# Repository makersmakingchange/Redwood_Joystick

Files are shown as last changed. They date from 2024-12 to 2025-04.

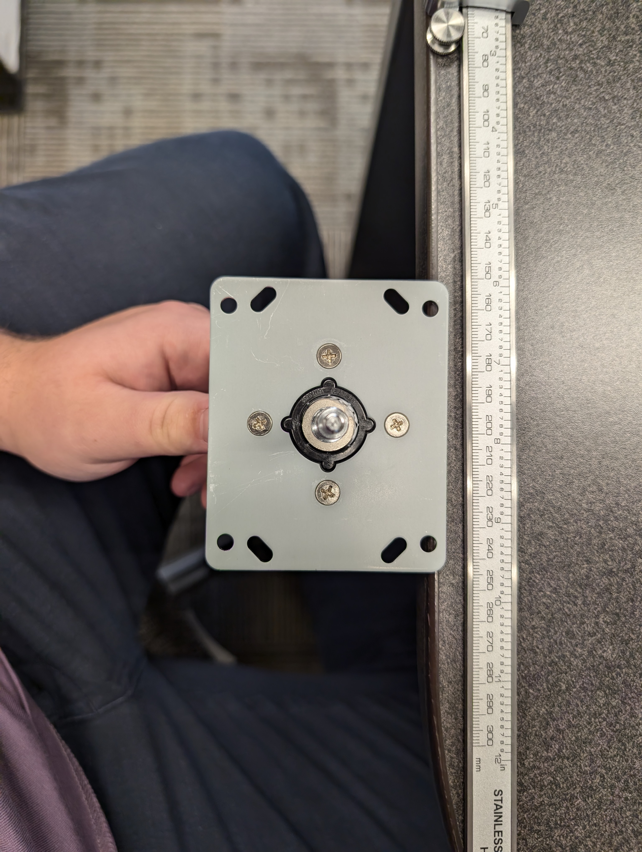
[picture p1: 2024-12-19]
Photos/Reference_Images/hold hole reference.jpg

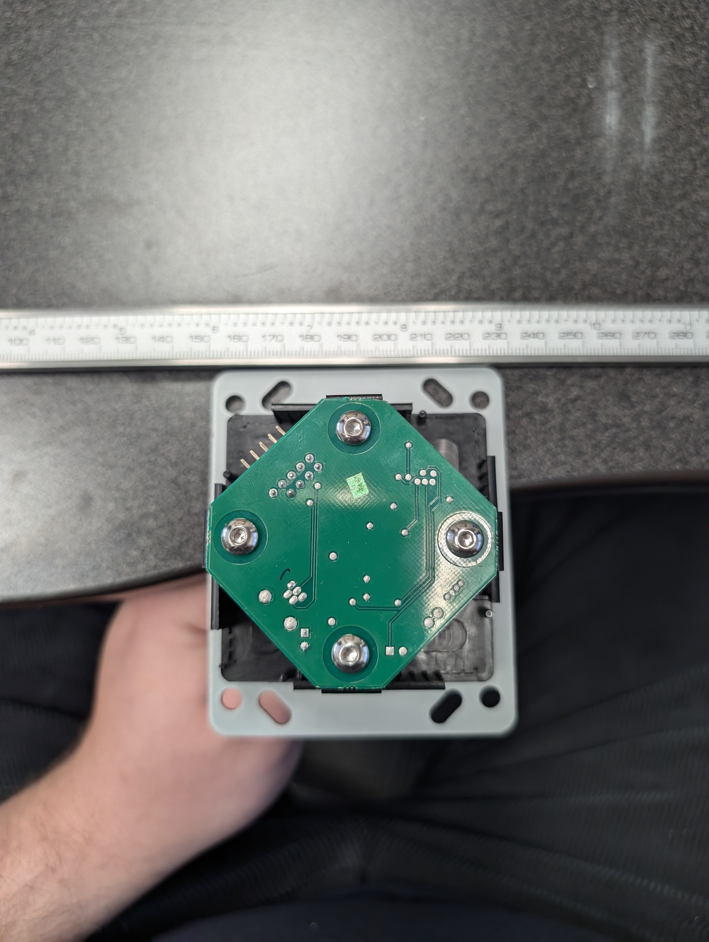
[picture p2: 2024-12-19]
Photos/Reference_Images/Reference Photo 2.jpg

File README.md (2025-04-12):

<!--- Open Source Assistive Technology: GitHub Readme Template Version 1.1 (2024-Mar-15)  --->

<!-- TITLE -->
# Redwood Joystick

<!--- SUMMARY ---> 
The Redwood Joystick is designed for users with gross motor movement and high strength, providing a durable and reliable solution for adaptive gaming and digital access. With its USB connection, it functions seamlessly as a computer mouse or gamepad, offering flexibility to suit your needs. Compatible with our [Oak Compact Joystick toppers](https://github.com/makersmakingchange/Oak-Compact-Joystick/tree/main/Build_Files/3D_Printing_Files/Toppers), it can be customized with options like goalpost or concave designs for personalized comfort. The joystick’s robust construction ensures it withstands heavy use, while its mounting adapters allow secure attachment to 1/4-20 mounting arms and 1-inch RAM mounts, ensuring a stable and accessible setup in any environment.

The device is comprised of off-the-shelf electronics, hardware, and 3D printed parts. The design uses the Ultimarc [Ultrastik analog 360 joystick](https://www.ultimarc.com/arcade-controls/joysticks/ultrastik-360-oval-top-clone/) in a robust 3D printed enclosure.

The overall cost of materials is about $97 CAD. You will need to pay customs fees if you are outside of the USA and the product can take up to 1 week to ship. Consider this in comparison to the other parts that are more readily available.

Picture of Redwood Joystick.

## More info at
- [Makers Making Change Assistive Device Library Listing](https://www.makersmakingchange.com/s/product/redwood-joystick/01tJR000006skOzYAI)

## How to Obtain the Device
### 1. Do-it-Yourself (DIY) or Do-it-Together (DIT)

This is an open-source assistive technology, so anyone is free to build it. All of the files and instructions required to build the device are contained within this repository. Refer to the Maker Guide below.

### 2. Request a build of this device

You may also submit a build request through the [Makers Making Change Assistive Device Library Listing](https://www.makersmakingchange.com/s/product/redwood-joystick/01tJR000006skOzYAI) to have a volunteer maker build the device. As the requestor, you are responsible for reimbursing the maker for the cost of materials and any shipping.

### 3. Build this device for someone else

If you have the skills and equipment to build this device, and would like to donate your time to create the device for someone who needs it, visit the [MMC Maker Wanted](https://makersmakingchange.com/maker-wanted/) section.

## Build Instructions

### 1. Read through the Maker Guide

The [Maker Guide](/Documentation/Redwood_Joystick_Maker_Guide.pdf)  contains all the necessary information to build this device, including tool lists, assembly instructions, programming instructions (if applicable) and testing.

### 2. Order the Off-The-Shelf Components

The [Bill of Materials](/Documentation/Redwood_Joystick_BOM.csv) lists all of the parts and components required to build the device.

### 3. Print the 3D Printable components

All of the files and individual print files can be in the [/Build_Files/3D_Printing_Files](/Build_Files/3D_Printing_Files/) folder.

## How to improve this Device
As open source assistive technology, you are welcomed and encouraged to improve upon the design. 

## Files
### Documentation
| Document             | Version | Link |
|----------------------|---------|------|
| Design Rationale     | 1.0     | [Redwood_Joystick_Design_Rationale](/Documentation/Redwood_Joystick_Design_Rationale.pdf)     |
| Maker Guide          | 1.0     | [Redwood_Joystick_Maker_Checklist](/Documentation/Redwood_Joystick_Maker_Guide.pdf)     |
| Bill of Materials    | 1.0     | [Redwood_Joystick_Bill_of_Materials](/Documentation/Redwood_Joystick_BOM.csv)     |
| User Guide           | 1.0     | [Redwood_Joystick_User_Guide](/Documentation/Redwood_Joystick_User_Guide.pdf)    |
| Changelog            | 1.0     | [Changelog](CHANGES.txt)     |

### Design Files
<!---
DESIGN FILES
Include a copy of the original design files to facilitate easy editing and customization. Consider also including a generic format (e.g., STEP)
--->
 - [CAD Files](/Design_Files/CAD_Design_Files)

<!---
BUILD FILES
Include a copy of the build files intended for manufacturing. This may include svg files for laser cutting, stl files for 3d printing, Gerber files for custom PCBs, and Arduino files for custom firmware
--->
### Build Files
 - [3D Printing Files](/Build_Files/3D_Printing_Files)

<!---
ATTRIBUTION
Provide any necessary attribution for designs or components that are included in the device or as part of the project.
--->
## Attribution

 - Designed by Neil Squire Society / Makers Making Change.

<!--- This is the attribution for the template. --->
 - The documentation template was created by Makers Making Change / Neil Squire Society and is used under a CC BY-SA 4.0 license. It is available at the following link: [https://github.com/makersmakingchange/OpenAT-Template](https://github.com/makersmakingchange/OpenAT-Template)

<!---
CONTRIBUTORS
List the names of the people that contributed to the design. This could include the original source of the idea, designers, testers, documenters, etc.
--->
### Contributors

Designers:
 - Tyler Fentie

<!---
LICENSE
Add the year(s) for the copyright and the Designer Name. You may use the standard set of open licenses or choose your own for the hardware, software, and accompanying materials.
--->
## License
Copyright (c) 2025 Redwood Joystick.

This repository describes Open Hardware:
 - Everything needed or used to design, make, test, or prepare the Redwood Joystick is licensed under the [CERN 2.0 Weakly Reciprocal license (CERN-OHL-W v2) or later](https://cern.ch/cern-ohl ) .
 - All software is under the [GNU General Public License v3.0 (GPL-3.0)](https://www.gnu.org/licenses/gpl.html).
 - Accompanying material such as instruction manuals, videos, and other copyrightable works that are useful but not necessary to design, make, test, or prepare the Redwood Joystick are published under a [Creative Commons Attribution-ShareAlike 4.0 license (CC BY-SA 4.0)](https://creativecommons.org/licenses/by-sa/4.0/) .

You may redistribute and modify this documentation and make products using it under the terms of the [CERN-OHL-W v2](https://cern.ch/cern-ohl).
This documentation is distributed WITHOUT ANY EXPRESS OR IMPLIED WARRANTY, INCLUDING OF MERCHANTABILITY, SATISFACTORY QUALITY AND FITNESS FOR A PARTICULAR PURPOSE.
Please see the CERN-OHL-W v2 for applicable conditions.

Source Location: https://github.com/makersmakingchange/Redwood_Joystick

----

<!-- ABOUT MMC START -->
## About Makers Making Change
[Makers Making Change Logo](https://www.makersmakingchange.com/)

Makers Making Change is a program of [Neil Squire](https://www.neilsquire.ca/), a Canadian non-profit that uses technology, knowledge, and passion to empower people with disabilities.

Makers Making Change leverages the capacity of community based Makers, Disability Professionals and Volunteers to develop and deliver affordable Open Source Assistive Technologies.

 - Website: [www.MakersMakingChange.com](https://www.makersmakingchange.com/)
 - GitHub: [makersmakingchange](https://github.com/makersmakingchange)
 - Bluesky: [@makersmakingchange.bsky.social](https://bsky.app/profile/makersmakingchange.bsky.social)
 - Instagram: [@makersmakingchange](https://www.instagram.com/makersmakingchange)
 - Facebook: [makersmakechange](https://www.facebook.com/makersmakechange)
 - LinkedIn: [Neil Squire Society](https://www.linkedin.com/company/neil-squire-society/)
 - Thingiverse: [makersmakingchange](https://www.thingiverse.com/makersmakingchange/about)
 - Printables: [MakersMakingChange](https://www.printables.com/@MakersMakingChange)

### Contact Us
For technical questions, to get involved, or to share your experience we encourage you to [visit our website](https://www.makersmakingchange.com/) or [contact us](https://www.makersmakingchange.com/s/contact).
<!-- ABOUT MMC END -->

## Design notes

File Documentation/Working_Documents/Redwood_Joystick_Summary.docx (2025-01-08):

# Overview

The Device Summary is intended to be a detailed summary of the device, product and maker information for the Redwood Joystick, making it easier to add to the Makers Making Change website. It is intended for anyone who will view the device listing.

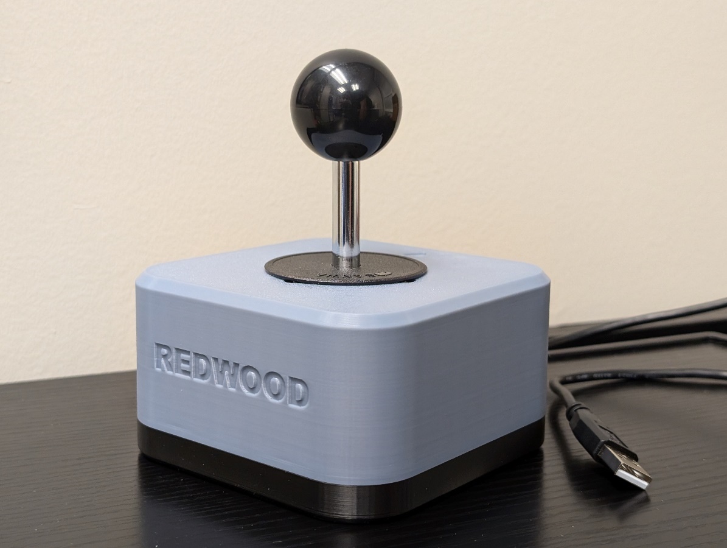
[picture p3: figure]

# Product Information

## Product Name

Redwood Joystick

## Device Category

| Adapted Toys
| Aids for Daily Living (ADL)
| Assistive Switches
| Communication Aids (AAC)
| Computer Access
| Environmental Controls
x | Gaming
| Keyguard
| Kits
| LipSyncs
| Mounting
| Recreation and Leisure
| Seating and Positioning
| Switch Interfaces
| Writing Aids
x | joysticks

## User Value Statement

The Redwood Joystick is a robust analog USB joystick designed for users with gross motor movement and high strength. Its durable build ensures reliable performance for digital access and adaptive gaming.

## Designer

Tyler Fentie – Makers Making Change

# Device Information

## Overview

The Redwood Joystick is designed for users with gross motor movement and high strength, providing a durable and reliable solution for adaptive gaming and digital access. With its USB connection, it functions seamlessly as a computer mouse or gamepad, offering flexibility to suit your needs. Compatible with our Oak Compact Joystick toppers, it can be customized with options like goalpost or concave designs for personalized comfort. The joystick’s robust construction ensures it withstands heavy use, while its mounting adapters allow secure attachment to 1/4-20 mounting arms and 1-inch RAM mounts, ensuring a stable and accessible setup in any environment.

## Disability Type

x | Agility / Dexterity
x | Arthritis
x | Cognitive
| Hearing
x | Mobility
x | Pain
x | SCI
| Vision
| Other

## Disability Type Description

The Redwood Joystick is ideal for individuals with strong gross motor movement but limited fine motor control or targeting accuracy. This includes users with conditions such as cerebral palsy, some forms of muscular dystrophy, or individuals with spinal cord injuries or post-stroke conditions who retain significant strength in larger muscle groups. Designed for those who can manage more forceful or broad movements, the joystick offers a durable, stable solution for both adaptive gaming and digital access.

## How To Use

The Redwood Joystick is simple to use. Connect the joystick’s USB Type A input to a compatible device, such as a phone, computer, Xbox Adaptive Controller, or Hori Flex Controller. See user guide for full compatibility. Once plugged in, the joystick allows you to control the device mouse or joystick input. It can be used for navigating digital interfaces, gaming, or other applications requiring joystick input, providing a reliable and easy-to-use solution.

## Estimated Cost

The estimated material cost of the device for a single build:

| $0 - $10
| $11 - $25
| $26 - $50
x | $51 - $100
| $101 - $250
| $250+

## Attribution

Designed by Neil Squire Society / Makers Making Change

Contributors

- Tyler Fentie, Neil Squire. Design and documentation.

The documentation template was created by Makers Making Change / Neil Squire and is used under a CC BY-SA 4.0 license. It is available at the following link: https://github.com/makersmakingchange/OpenAT-Template

Design inspired by SCCR Rehabilitation Engineering: https://www.printables.com/model/268854-ultrastik-analog-joystick-enclosure

# Maker Information

## Project Skills

x | 3D Printing
| Custom PCB
| Electronics
| Laser Cutting
| Mechanics
| Software
| Soldering
| Woodworking
| Other

## Skills Description

3D print the provided enclosure files and assemble the components using common hand tools (Screwdriver and plyers). With basic assembly skills and access to a 3D printer, you can quickly create a fully functional Redwood Joystick.

## Tools Needed

| 3D Printer
x | Common Hand Tools
| Common Power Tools
| Laser Cutter
| Soldering Iron
| Specialized Tooling

## Print time (hrs)

3hrs 2min

## Assembly time (hrs)

0.5hrs

## Build Instructions

To build the Redwood Joystick, start by 3D printing the enclosure using the provided design files. Once the enclosure is ready, gather the joystick components and common hand tools such as a screwdriver and pliers. Assemble the joystick by attaching the Ultimarc UltraStik 360 to the enclosure, securing the wiring, and mounting any desired Oak Compact Joystick toppers using the Topper Adapter Nut. If needed, attach the mounting adapters for RAM or 1/4-20 camera mounts. Finally, connect the joystick via USB to test functionality and ensure smooth operation. The process is straightforward, requiring only basic tools and assembly skills.

- Top and bottom 3D printed enclosure
- Ultimarc Ultrastik 360
- Optional: Oak toppers
- Optional: Mounting adapters for RAM or ¼-20 Camera mount

## Download Link

https://github.com/makersmakingchange/Redwood_Joystick/archive/refs/heads/main.zip

## Project Link

https://github.com/makersmakingchange/Redwood_Joystick

# License

## License

Hardware: CERN OHL-W

Documentation: CC BY SA 4.0

© 2024 by Neil Squire. This work is licensed under the CC BY SA 4.0 License: http://creativecommons.org/licenses/by-sa/4.0 Files available at https://github.com/makersmakingchange/Redwood_Joystick/tree/main Page 1 of 2

V1.0 | Dec 2024 Redwood Joystick Summary

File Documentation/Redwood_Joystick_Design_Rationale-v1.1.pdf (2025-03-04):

V1.0 | August 2024

## Redwood Joystick

## DESIGN RATIONALE

© 2024 by <Author>.
This work is licensed under the CC BY SA 4.0 License: http://creativecommons.org/licenses/by-sa/4.0
Files available at <Replace with MMC Library Link> | Page 1 of 43

### Introduction

- There are several joystick options in the MMC library, but there currently is not a bigger or more durable than the Oak Joystick
- The Ultrastik Joystick is bigger option but does not come with an enclosure.
- Several enclosure options exist, but are either commercial or not optimized for makers.

User focus:
- Gamers with gross motor movement and high strength

## DESIGN RATIONALE

Files available at <Replace with MMC Library Link> | Page 2 of 43

### Research

### Commercial options

Title | Quadstick Ultrastik 360
Link | Quadstick (https://www.quadstick.com/shop/ultimarc-utrastik-360-enclosure)
Author | Quadstick - Fred
License | Commercial
Cost | $204 CAD
Notes | Most popular solution for getting Ultrastik’s in North America
Title | Ultra-Stik
Link | https://oneswitch.org.uk/page/shop-ultra-stik
Author | Barrie Ellis – OneSwitch
License | Unknown
Cost | $174 CAD
Notes | Most popular solution for getting Ultrastik’s in Europe

### DIY designs

Title | OneSwitch – DIY [Instructions ONLY]
Link | OneSwitch - DIY (https://oneswitch.org.uk/art.php?id=73)
Author | Barrie Ellis – OneSwitch
License | N/A
Cost | Free
Test Build (Y/N) | N/A
Add to Library (Y/N) | No but credit them in this design
Notes
Title | UltraStik – SCCR
Link | SCCR Printables (https://www.printables.com/model/268854-ultrastik-analog-joystick-enclosure)
Author | SCCR – Rachelle Bernier
License | CC attribution-shareAlike
Cost | $100 CAD
Test Build (Y/N) | N/A
Add to Library (Y/N) | No but credit them in this design
Notes
Title | Ultrastik - Gearhead
Link | Gearhead Printables (https://www.printables.com/model/510023-housing-for-ultimarc-ultrastik-360)

## DESIGN RATIONALE

Files available at <Replace with MMC Library Link> | Page 3 of 43
Author | Gearhead (printables username)
License | GNU v2.0
Cost | $100 CAD
Test Build (Y/N) | N/A
Add to Library (Y/N) | N
Notes

## DESIGN RATIONALE

Files available at <Replace with MMC Library Link> | Page 4 of 43

### Requirements

### Goals

G01 | Act as a larger and durable form factor for our joystick line.
G02 | Provide an option for users who are breaking the internals of the Oak Joystick.
G03 | Maker manufacturable in quantities of one.
G04 | The use of support material in 3d printed components should be minimized.
G05 | The number of different filament types should be minimized.
G07 | Material costs should be minimized as to provide a low cost options (Less than or equal to $100 CAD)

### Functional Requirements

F01 | The joystick shall be usable from a the distance given by the USB cable supplied by UltraStik
F02 | The joysticks shall be compatible with the Xbox Adaptive Controller.
F03 | Joysticks shall be PC compatible.
F04 | The joystick shall denote use orientation.
F05 | The joystick shall have a range of easily interchangeable toppers.
F06 | Toppers shall not interfere with the regular physical motion of the joystick.
F07 | Toppers shall have a secure connection to the joystick.
F08 | The joystick shall be designed to be used by either hand.
F09 | Joystick shall remain stable when in use.
F10 | The housing shall protect internal components from outside sources.
F11 | Joystick designs shall support camera mounting styles.
F12 | Joystick designs shall support hook and loop fastener mounting styles.
F13 | Joystick designs shall support tabletop mounting styles with no fasteners.
F14 | Enclosure shall work with the Ultrastik joystick component

### Non-functional Requirement

NF01 | Documentation should be maintainable with the use of commonly available software.
NF02 | Documentation must be available in a digital format.
NF03 | Documentation must be printable.
NF04 | Documentation, code, and hardware must have appropriate open-source licenses.
NF05 | Instructions must be provided for using joystick with XAC for gaming
NF06 | Instructions must be provided for using joystick with PC/Phone/Tablet for gaming
NF07 | Instructions must be provided for using joystick with PC/Phone/Tablet for digital access

### Constraints

C01 | Joystick must be maker manufacturable.
C02 | Not for use with mobility devices.
C03 | The joystick shall be based on the commercially available Ultrastik 360 Analog Joystick.
C04 | The Ultrastik 360 Analog Joystick has an approximate activation force of 298 grams.

## DESIGN RATIONALE

Files available at <Replace with MMC Library Link> | Page 5 of 43
C05 | The Ultrastik 360 Analog Joystick has an X and Y axis range of ±15.5°
C06 | The Ultrastik 360 Analog Joystick has a linearity of TBR (no info from manufacturer)
C07 | The Ultrastik 360 Analog Joystick has a mechanical lifecycle of TBR (no info from manufacturer)
C08 | The Ultrastik 360 Analog Joystick has an operating temperature range of TBR (no info from manufacturer)
C09 | 3D printed components shall be printable within a 180x180x180mm print volume.

## DESIGN RATIONALE

Files available at <Replace with MMC Library Link> | Page 6 of 43

### Ideation

- Prevent using screws coming from the top enclosure if possible
- This may be able to be prevented with the use of the dust cover. Need to investigate
- The top of the joystick component should allow room for the dust cover
- No easily source able size of bolt will allow for a design where the bolt comes through the bottom side of the joystick component into a enclosure without spacers
- Toppers
- Use Oak toppers by adapting the 3D printed nut to fit onto the ultrastik

## DESIGN RATIONALE

Files available at <Replace with MMC Library Link> | Page 7 of 43

### Conceptual Design

Initial conceptual design was conducted using a modified version of the SCCR Printables (https://www.printables.com/model/268854-ultrastik-analog-joystick-enclosure) ultrastik enclosure. The following was modified:

- Insert holes on the top enclosure for the bolts. These were altered to fit M5 bolts.
- Chamfers were also added for ease of assembly
- Spacers were added for the M5x12 bolts to allow the joystick component to sit at the same height as the SCCR option.
- General fillets were added to the top part of the enclosure to ensure force distribution and prevent shearing of 3D printed parts
- The topper nut from the Oak Joystick was modified to fit a M6 nut inside to secure the toppers to the Ultrastik component.

### Concept 1 – SCCR Modification

Assembly
Assembly is compromised of the following parts:
1. Ultrastik joystick unit
a. USB-Mini to USB A cable
b. Ball topper
c. Dust washer cover
2. Top Enclosure
3. Bottom Enclosure
4. 4x M5x12 bolts
5. #?? Machine Screws
6. 4x Bolt spacer
7. 1x M6 nut
8. 1x Joystick topper adapter

Images of parts:

## DESIGN RATIONALE

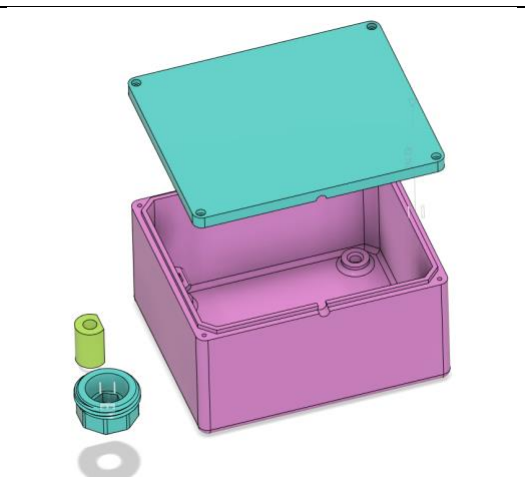
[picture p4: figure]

Files available at <Replace with MMC Library Link> | Page 8 of 43

The steps to assembly are:

1. Put the dust cover washer onto the joystick component
2. Put the joystick component into the top base
3. Line up the bolt holes with the holes on the joystick component
4. Place the spacer between the bolt holes and M5 bolt
5. Screw down all M5 bolts to secure the joystick component to the top of the enclosure
6. Attach the USB cable to the joystick component and place the cable zip tie it to the strain relief attachment
7. Attach the bottom of the component with the small machine screws

## DESIGN RATIONALE

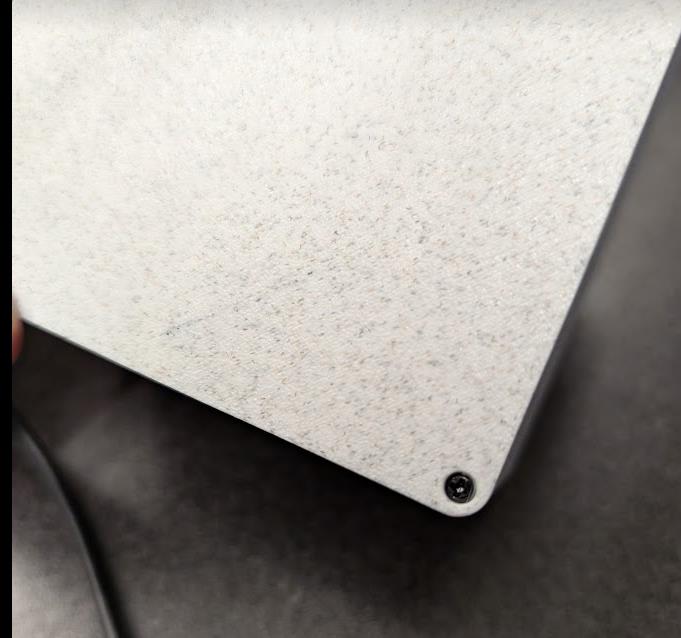
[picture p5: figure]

Files available at <Replace with MMC Library Link> | Page 9 of 43

Bottom enclosure

- These are quite close to the edge and are likely not big enough to keep the base secured to the top part of the enclosure if someone had it fastened to a mount or table with hook and loop.

Top Enclosure

- Left picture is without dust cover and right is with dust cover. The dust cover slides underneath nicely but is quite loud. Consider making a track for it to follow underneath to prevent rocking.
- Dust cover adds a higher quality feel and helps prevent fluids, dust, and grime getting inside the joystick. This is also standard for most arcade style fighting joysticks.

## DESIGN RATIONALE

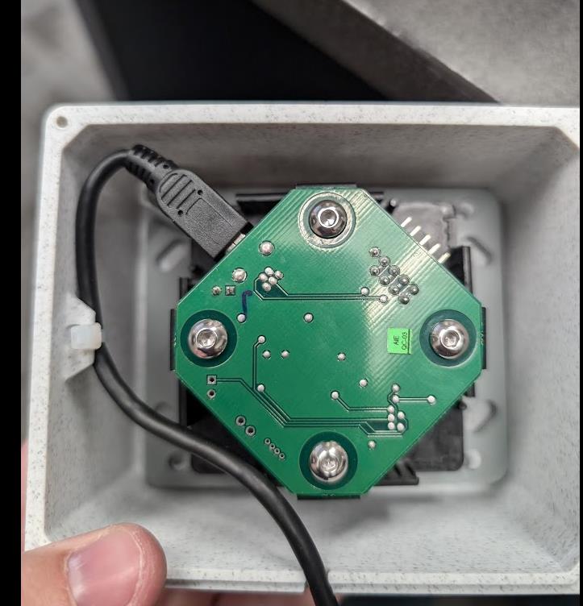
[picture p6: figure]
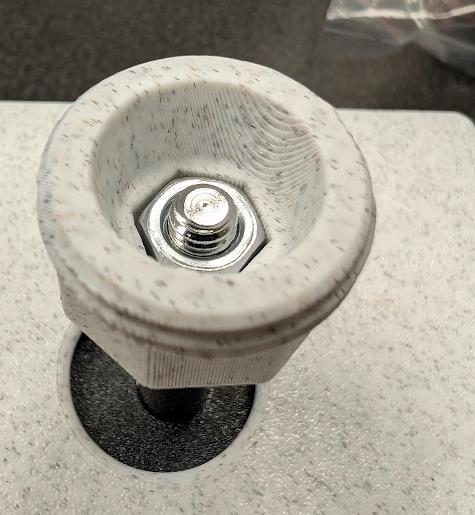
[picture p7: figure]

Files available at <Replace with MMC Library Link> | Page 10 of 43
- Bolt hole locations for the four corners of the joystick component are very close but could be lined up better.

Toppers

- M6 nut fits nicely inside the joystick topper adapter.
- A 2mm gap was chosen between the bottom of the joystick adapter and start of threads on the M6 nut.
- This choice worked well as the base of the joystick topper adapter has strength in the bottom to resist puncture from joystick topper.

## DESIGN RATIONALE

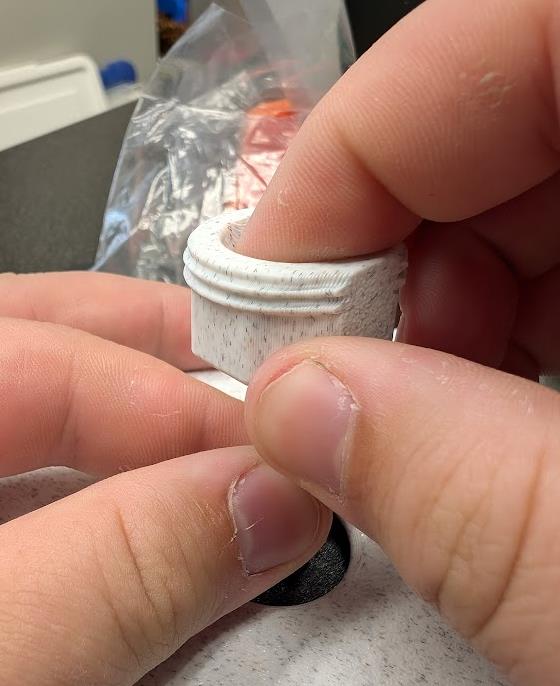
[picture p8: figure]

Files available at <Replace with MMC Library Link> | Page 11 of 43
- Assembly of the joystick topper adapter on the threads of the joystick component could be improved
- When first starting the threading, you have to push the joystick topper adapter up and with the other hand push the nut down into the cutout for it.
- Once threads are started, to screw down you have to lift up on the joystick topper adapter at the same time
- This can be improved with a lid or some way to more permanently fix the M6 nut into the joystick topper adapter.

## DESIGN RATIONALE

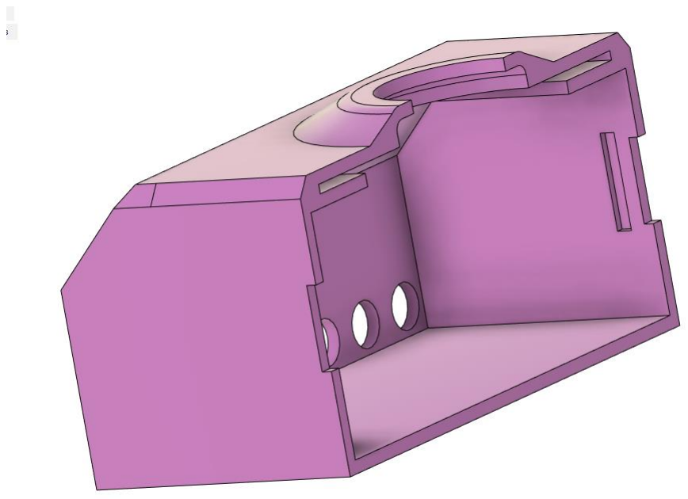
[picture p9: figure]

Files available at <Replace with MMC Library Link> | Page 12 of 43
- All Oak joystick toppers fit as expected onto the joystick topper adapter
- The sizing of the toppers is appropriate for the joystick and does not restrict movement.

### Concept 2 – Vertical Split Housing

Snap Fit Enclosure
- Also designed by SCCR, a modified version of the enclosure was made for assistive switch port and snap fit with a vertical cut. Photo below:
- The top plate of the Ultrastik joystick can be used to fix the vertical location of the joystick and the enclosure can snap around it to lock it into position

## DESIGN RATIONALE

Files available at <Replace with MMC Library Link> | Page 13 of 43

Non Snap Fit
- Same idea except using fasteners to attach the two sides of the enclosure together

### Concept 3 – Built in Spacers

Similar to the Gearhead 3D print model that is on Printables, there could be a version where the spacers are attached to the enclosure. See photo below:

- We would want to avoid the bolts being attached through the top of the enclosure to prevent abrasion to the user.

### Prototyping

Concept 1 was chosen to be the first MVP design to get to the Movement Centre for testing as the designer was heading there for GAME Checkpoint training. This was designed in CAD, tested, and trialed during the Movement Centre.

### Recreating the Ultrastik Joystick Component

There is not currently an official or verified open-source CAD model of the Ultrastik Joystick. As such, a CAD model was designed with a physical unit available to the designer. Utilizing physical measurements with a caliper and using the canvas feature in Fusion an approximate model was created.

## DESIGN RATIONALE

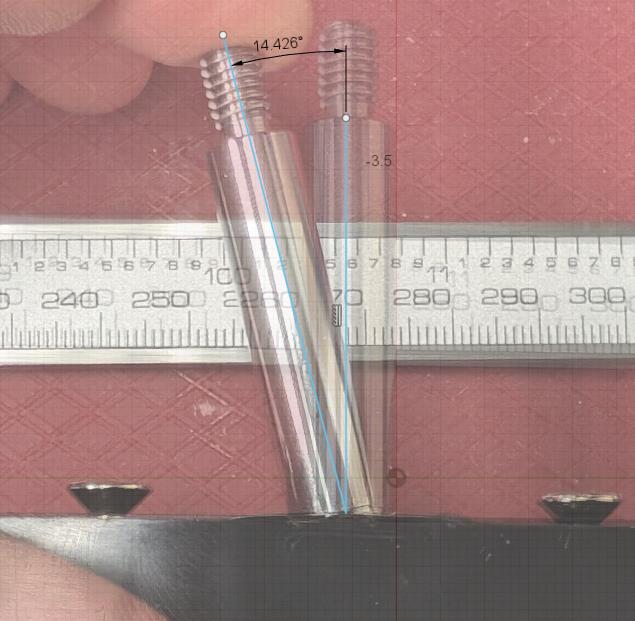
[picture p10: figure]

Files available at <Replace with MMC Library Link> | Page 14 of 43

Key measurements and features of the Ultrastik can be seen below:

- Outer mounting holes on the mounting plate fit size M5 bolts.
- Screws holding the mounting plate onto the joystick component is M4x10 countersunk.

### ROM of Joystick

Measured in person with a physical unit using a protractor to be approximately 16.5 degrees. To verify approximation, photos were added to Fusion and the angle was estimated there to be 14.426 degrees. The different is taken to be approximately 15.46 degrees and rounded up to 15.5 degrees.

## DESIGN RATIONALE

Files available at <Replace with MMC Library Link> | Page 15 of 43

### Joystick Position Relative to Top Enclosure

If there is some type of attachment mechanism inside the top enclosure such as imbedded nuts, screw holes, etc there may be distance between the top of the Ultrastik joystick and top enclosure. It is necessary to determine what the maximum distance would be allowed between the top of the Ultrastik joystick and upper enclosure.

The main considerations we have to design for here are:

1. When any of the Oak sized toppers are added, they do not collide with the top of the enclosure
2. Have as much of the stick that is protruding out of the top of the enclosure as possible to align with the other standard commercial options.
3. It does not restrict with the ROM of the device in any way.

For reference, SCCR’s enclosure has a 3.5 mm distance between the Ultrastik mounting plate and inner top of the enclosure.

Whereas the Gearhead, One Switch, and Quadstick designs attach the joystick with screws from the top of the enclosure resulting in a 0 mm distance between the Ultrastik mounting plate and inner side of the top of the enclosure. See the Gearhead example below:

## DESIGN RATIONALE

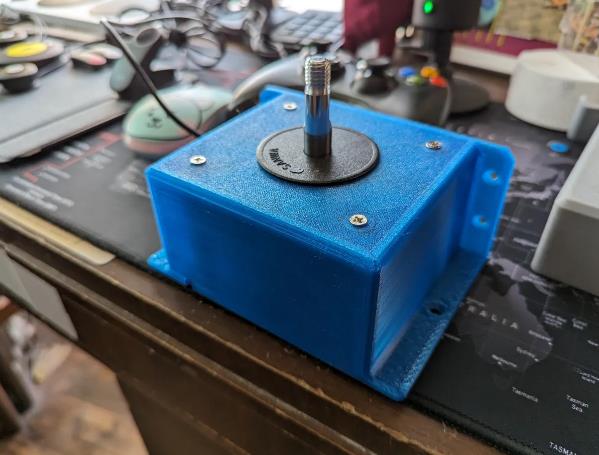
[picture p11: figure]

Files available at <Replace with MMC Library Link> | Page 16 of 43

The unit I tested with at the Movement Centre used a 3.5 mm distance like the SCCR design (see testing notes below). This distance did not cause any undesirable effects regarding the three considerations above.

### Testing

### Movement Centre Feedback

- Tested with 4 gamers and 4 clinicians from the Movement Centre during GAME Checkpoint training and open house.
- Out of the 4 gamers we tested with, 2 of them found it useful. The other 2 needed shorter joysticks such as the Spruce/Oak
- All 4 clincians used it to trial adaptive gaming setups.

Feedback:

## DESIGN RATIONALE

Files available at <Replace with MMC Library Link> | Page 17 of 43
- For the 2 gamers the form factor worked for, this was the joystick of choice out of the Oak, Spruce and Ivy.
- Clinicians liked the larger form factor and that it was compatible with the same toppers.
- Both clinicians and gamers disliked that the post of the Ultrastik joystick spins. This was difficult if the gamer did not have stability in their wrist or arm to keep the joystick topper straight.
- Toppers like the stick or ball were opted for instead of directional toppers like the goalpost.

### 3D printing Feedback

- After first initial print/test with the Movement Centre, clear improvements were identified. Wait until these improvements are made on the model until sending to Josie for 3D printing feedback.

### Detailed Design

### Style of Top Enclosure

Attachment of Joystick Unit to Enclosure
There are a few options that were considered when thinking about the attachment of the Ultrastik unit to the enclosure. First lets consider the options and criteria to begin to evaluate. Here are the methods of attachment:
1. Using the included M4x10 Machine Screws used to attach the Ultrastik mounting plate to the electronic housing as an attachment to the top face.
2. Use short (<5mm) M5 machine screws to attach through Ultrastik Mounting plate to housing from inside
3. Use a commonly available M5 machine screws to attach through the Ultrastik mounting plate to housing from inside with a bottom enclosure that has integrated spacers. Uses one M5 set of screws for attachment.
4. Use M5 machine screws through the top of the enclosure and a nut on the other side of the mounting plate to secure.
5. Use a snap fit or alternatives such as glue, tape, etc.
6. Using a top, bottom, and spacer 3D printed component that can sandwich between the top and bottom enclosures. Differs from option 3 as spacer is its own part.

The criteria that these options will be evaluated against were determined by the key considerations for this specific device.

- Consumables - We currently do not have any M5 machine screws in our common parts list so this is not a consideration to revolve the design around current stock. This allows us freedom for design while using the least number of consumables as possible.

## DESIGN RATIONALE

Files available at <Replace with MMC Library Link> | Page 18 of 43
- Strength – This will be the heavy duty offering of our joystick line. It must be both robust from the forces acting on the stick and where the mounting platform will be.
- Minimum thread engagement must be 1 times the nominal diameter which is referenced from Nord Lock. (https://www.nord-lock.com/learnings/bolting-tips/2015/the-experts-thread-engagement-in-a-tapped-hole/) Therefore 5 mm for the M5 and 4 mm for the M4.
- User Interaction/Ergonomics – Size, smooth top surface, and other considerations are important.
- Assembly complexity – Not as important as this will likely not be featured in build events due to cost.

The options above were evaluated based off of the criteria. A full decision matrix was not completed due to my own bias. Therefore, a straightforward reasoning was noted below to show a clear thought process:

Option | Evaluation against Criteria
1 | • | Consumables:
| | • Machine screws for the base component to be connected to the top enclosure.
- Strength:
| | • Given this is a threaded connection, it will be quite secure given the M4 machine screw will have sufficient thread engagement
- User Ergonomics:
| | • This would require screws to enter through the top of the enclosure which bring up other design considerations to prevent abrasions to user. ▪ A cover could be considered for the top screws if they are

imbedded more into the top of the device to prevent this.
| | • The base of the joystick will be smaller than if the mounting bracket is used. More testing would be required to see if this causes issues.
- Assembly complexity:
| | • This can result in the magnetic sensor at the bottom of the joystick being an incorrect distance away from the sensor resulting in drift and inconsistent results. This could be mitigated with quality checking units but considering the circumstances volunteer making I want to avoid this design.
2 | • | Consumables:
| | • Sourcing short M5 machine screws is very difficult. There are some on Amazon but with limited quantities. • No units to purchase on bulk sites such as Digikey.
- Strength:
| | • It could be difficult to get the minimum thread engagement needed to keep the joystick close to the top of the enclosure.
- User Ergonomics:
| | • This would require screws to enter through the top of the enclosure which bring up other design considerations to prevent abrasions to user.

## DESIGN RATIONALE

Files available at <Replace with MMC Library Link> | Page 19 of 43
| • Even using a M5x5mm screw, the joystick is farther away from the top of the enclosure than desired. • Assembly complexity: • Lining up the machine screws in the right place with such a deep top enclosure can be challenging.
3 | • Consumables: • Only 4x M5 machine screws needed. • Strength: • It could be difficult to get the minimum thread engagement needed to keep the joystick close to the top of the enclosure similar to commercial products. • There is a single point of connection for the base and connection to joystick. The force is all being transferred from mounting and joystick are on these 4 machine screws. • User Ergonomics: • No effect on user ergonomics. • Assembly complexity: • Simple assembly as it will have guided path for machine screws.
4 | • | Consumables: • Requires nuts as well as machine screws.
- Strength:
| | • Strong connection as it does not include self tapping into plastic.
- User Ergonomics:
| | • This would require screws to enter through the top of the enclosure which bring up other design considerations to prevent abrasions to user. • Distance of mounting plate to top of the enclosure is a minimum
- Assembly complexity:
| | • To get a secure connection a socket would be required. This is not in the standard bill of materials • A nut catch could be added as an alternative, but this would add distance from the mounting plate to the top of the enclosure.
5 | • Consumables: • Glue, tape, etc • Strength: • This joystick is designed to be a more heavy duty style for those with limited fine motor movement. With this, strength of the user could be quite high so using other methods of connection are undesirable as they could not be strong enough to bear this force. • User Ergonomics: • Distance of mounting plate to top of the enclosure could be minimum. • Assembly complexity: • Depending on method, this could be quite simple with something like a snap fit or time consuming like glue.
6 | • Consumables:

## DESIGN RATIONALE

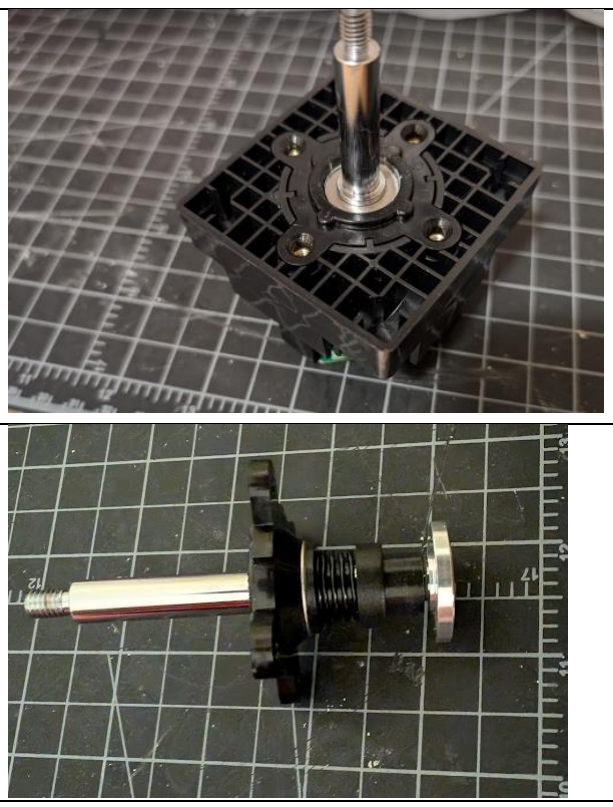
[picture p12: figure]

Files available at <Replace with MMC Library Link> | Page 20 of 43
- Requires an additional 3D printed component.
- Set of fasteners for base connection and top connection.
- Strength:
- Different points of contact for the base connection and joystick to the top enclosure.
- Spacer component can be designed in a way to optimize strength.
- User Ergonomics:
- No effects on user ergonomics.
- Assembly complexity:
- Could be difficult to hold everything together while attaching screws. Analyzing this, Option 1 was considered for the design approach as it will result in a very strong connection using the threaded holes. It also requires limited amount of consumables utilizing the ones coming with the unit. It will also allow more room within the housing by not using the mounting plate. This will make mounting the bottom enclosure easier. User ergonomics can also be mitigated easily with a cover for the screws.

Option 3 and 6 were also considered but Option 1 was chosen due to the advantage of less consumables, ease of assembly, and increased strength by using the threaded inserts provided by the joystick component.

Therefore, we can remove the mounting plate from the CAD and design moving forward. We are working with the joystick housing and the inner joystick mechanism along with 4 M4x10 countersink machine screws. Photos can be seen below.

## DESIGN RATIONALE

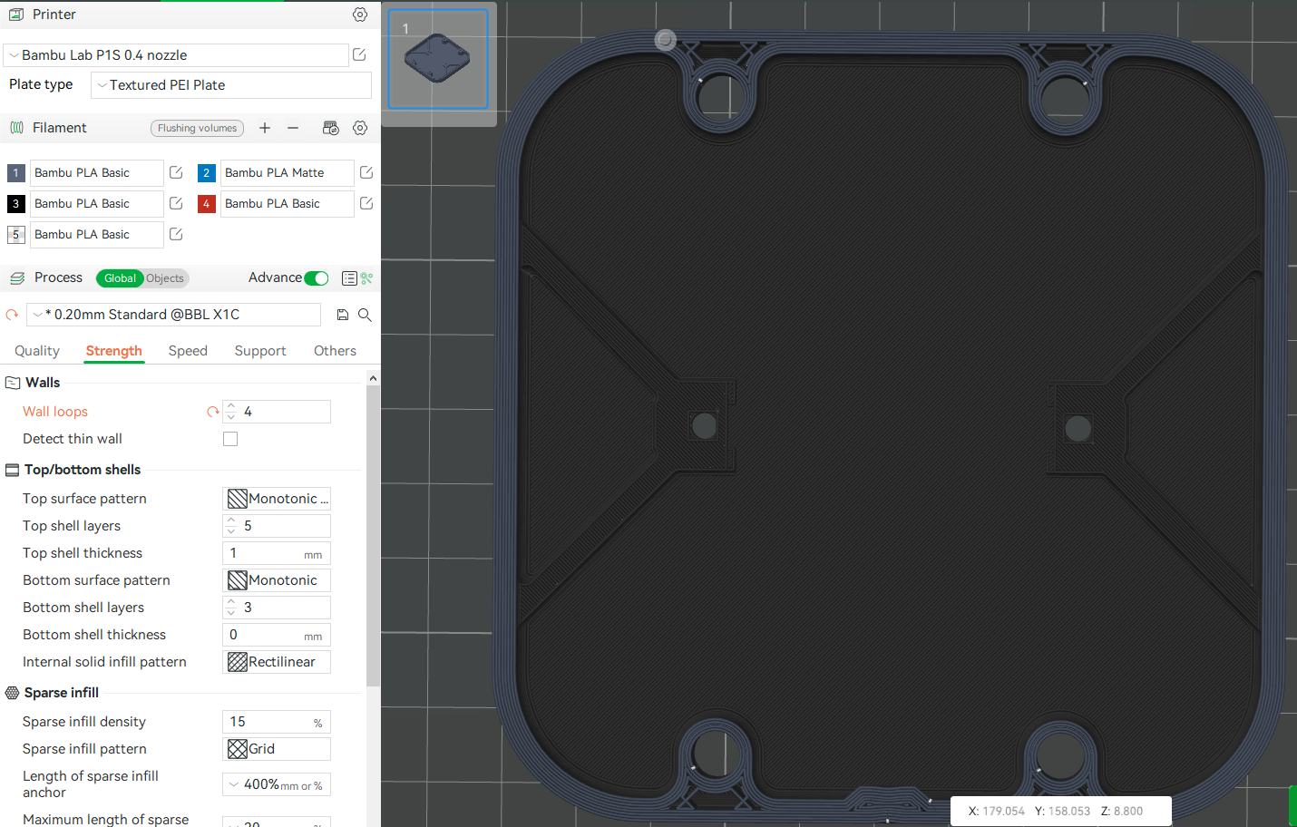
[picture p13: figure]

Files available at <Replace with MMC Library Link> | Page 21 of 43

### Design of Top Enclosure

Wall Thickness
- Side walls for all of our other current joysticks have a thickness of 1.6 mm which is approx. 4x times a 0.4 nozzle width. This joystick is intended to be more robust and because its highest failure point will likely be the layer lines, the wall thickness was doubled at 3.2 mm.

With this, at a wall loop set at 4 there will be no support material for the walls or around the screw holes on the top or bottom enclosure.

## DESIGN RATIONALE

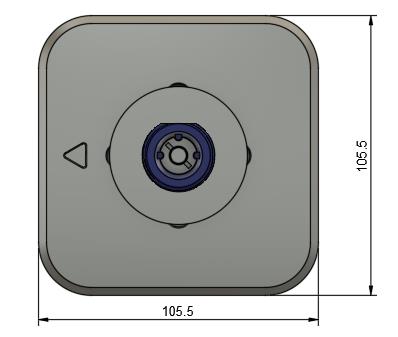
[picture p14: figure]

Files available at <Replace with MMC Library Link> | Page 22 of 43

Enclosure dimensions

105.5x105.5x58.7 mm (without stick)

105.5x105.5x107.1 mm (with stick and topper adapter)

- The length and width of this device is determined by the Ultrastik joystick dimensions without the mounting plate and the room needed inside the housings for strain relief and top to bottom enclosure attachment methods.
- Specifically, the overall length and width were determined to be 105.5 mm & 105.5 mm because of the clearance for the mounting between the top and bottom enclosures and space needed for the USB cable to enter the Ultrastik.
- The height was determined to be 105.5 mm because of the wall thickness of 3.2 mm on the top and bottom enclosures and the 58.7 mm height of the Ultrastik joystick housing (not including stick)

## DESIGN RATIONALE

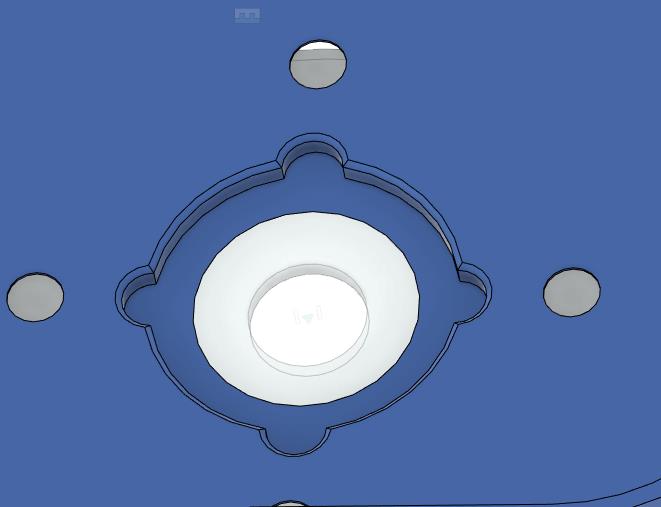
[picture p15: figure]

Files available at <Replace with MMC Library Link> | Page 23 of 43

Hole size for Joystick Stick to Exit
- The diameter of the exit hole for the joystick was chosen to be 19mm. This matches the diameter of the inner diameter of the protruding ring of the joystick component.
- A 2.25 mm deep insert was created on the inside of the enclosure to allow this protruding ring to fit inside. The shape was created by using a 0.25 mm offset to create a slight transitional fit.
- This will ensure proper hole alignment.
- The mounting plate the joystick comes with is 2mm thick so a 2mm clearance was required to ensure the same distance of the magnetic sensor as the original mounting plate.
- A small chamfer was added to aid in alignment when adding the Ultrastik Joystick to the housing.

Screw hole dimensions
- Using the hole tool the presets were chosen for a M4 countersunk, clearance tap, and flat drill point to the other side of the enclosure housing was chosen.
- The fit was specified to loose which changed the clearance tap from 4.5 mm to 4.8 mm

## DESIGN RATIONALE

Files available at <Replace with MMC Library Link> | Page 24 of 43

Exposed Screws
Originally, the thought was to create a part that could be inserted to cover the screw faces and become flush with the top face. However, after some print tests, sinking the screw faces 1 mm into the enclosure and use with the dust cover made the need for a cover irrelevant. There will be no risk for the user to come in contact with the screw faces unless the dust cover is not being used (incorrect usage) or a screw has become loose. More detail on the 1 mm insert and dust cover:
- The method chosen to address the exposed tops of the screws was to create a face 1 mm into the top of the joystick enclosure and create the M4 countersunk holes there. Then extrude a cut to expose the countersink 1 mm down. This results in the screws being 1 mm below the surface of the joystick.
- The dust cover also covers the majority of the screw faces.

## DESIGN RATIONALE

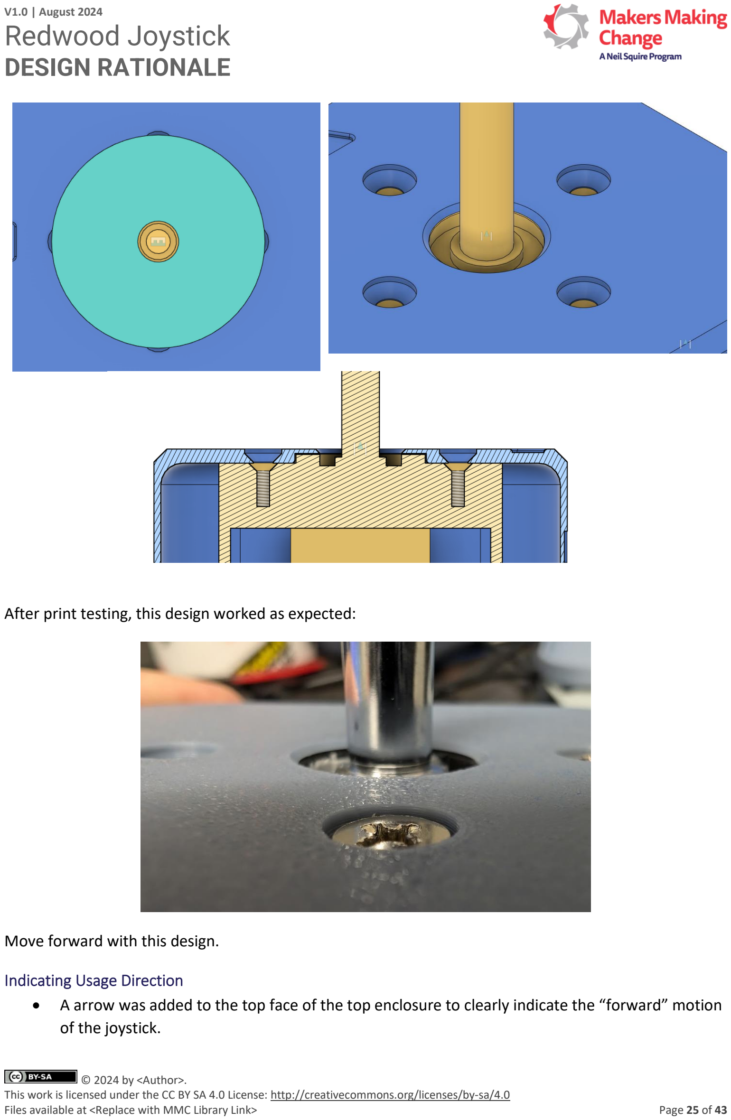
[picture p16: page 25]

Files available at <Replace with MMC Library Link> | Page 25 of 43

After print testing, this design worked as expected:

Move forward with this design.

Indicating Usage Direction
- A arrow was added to the top face of the top enclosure to clearly indicate the “forward” motion of the joystick.

## DESIGN RATIONALE

Files available at <Replace with MMC Library Link> | Page 26 of 43
- Similar sizes, fillets, and chamfers were chosen from previous MMC joysticks (Oak, Spruce, Aspen, etc).

Indicating Assembly orientation
It can be hard to determine how the ultrastik mechanism needs to be oriented so the USB cable is in the right place and therefore the directionality is right. Text was added to the inner face of the top enclosure to help the maker.

Ideally there would be a way to key this so the maker can not but the joystick in the wrong way but the Ultrastik is symmetrical. This text was chosen and along with the Maker Guide the user will be able to insert the joystick the right way.

Exit of cable
- A hole was added on the “rear” face of the joystick which will be away from the user and toward the device (computer or adaptive controller) when in use.
- The cable that comes with the Ultrastik has a diameter of 3.7 mm. As such, the hole was designed to be 4.2 mm to allow for a slight transition fit to add some friction for some added strain relief.
- The hole was created between the connection of the top and bottom enclosure to prevent the need for soldering/stripping wire to have the cable exit.
- Based on clinician and user feedback, the port of the USB on the Ultrastik is not accessible while the joystick is assembled. However, if a cable needs to be replaced, the base can be detached to swap them easily.
- A 5 mm fillet was added to smooth the exit and add a refined esthetic look.

## DESIGN RATIONALE

Files available at <Replace with MMC Library Link> | Page 27 of 43

Strain relief
- Inspiration was taken from the strain relief of the Oak joystick.
- The intention is for the user to slide a zip tie into the strain relief feature inside the top enclosure and use it to attach the provided USB cable.
- There was a 45 degree angle added to the feature so no supports will be needed when printing.
- A large fillet was added inside the slot of the feature to guide the zip tie to exit properly.
- Fillets with 2 mm radii were added to the outside of the feature to aid in printing and strength when force is applied to the cable externally.

Outer Chamfer
Set at 3 mm. The chamfer will prevent elephant foot. 3 mm was chosen by esthetics primarily.

## DESIGN RATIONALE

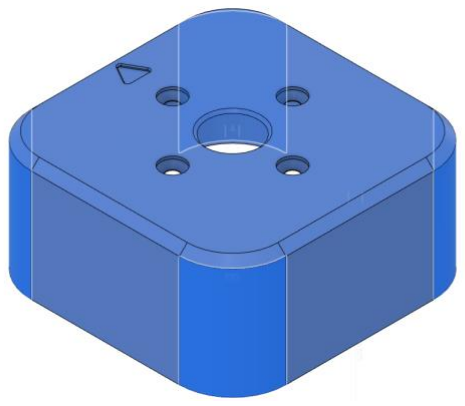
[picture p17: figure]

Files available at <Replace with MMC Library Link> | Page 28 of 43

Outer Fillet
All 4 corners are filleted on the housing. This is to allow for a more esthetic print and avoid sharp corners. Set at 20 mm determined primarily on esthetics.

Inner Fillet
A continuous 5 mm fillet was added to the inside of the top enclosure. This will help reduce strain at the edges of the print.

## DESIGN RATIONALE

Files available at <Replace with MMC Library Link> | Page 29 of 43

Attachment to Bottom Enclosure:
Because the device will be mounted from the base on hook and loop fasteners or on a mounting arm through the standard Open AT adapter, the forces acting between the bottom and top enclosures must be considered. With that, what type of attachment between the enclosures needs to be evaluated. See proposed options, evaluation criteria, and evaluation below:
1. Option 1 – Using the common screw part (#4 self-tapping 3/8" length) used in the Oak joystick with a similar features on the top and bottom enclosures. Self tapping into a plastic feature
2. Option 2 – Snap fit
3. Option 3 – Bolt/nut catch style. Using a 3D printed feature on the top enclosure as a nut catch. A bolt then will be inserted from the bottom enclosure.

The criteria that these options will be evaluated against were determined by the key considerations for this specific device.

- Consumables – Utilizing common parts or no parts are prioritized.
- Strength – This will be the heavy duty offering of our joystick line. It must be both robust from the forces acting on the stick and where the mounting platform will be.
- Assembly complexity – Not as important as this will likely not be featured in build events due to cost.

The options above were evaluated based off of the criteria. A full decision matrix was not completed due to my own bias. Therefore, a straightforward reasoning was noted below to show a clear thought process:

Option | Evaluation against Criteria
1 | • Consumables: • 4x #4 screws • Strength: • Self tapped into the 3D print. This has worked well in the Oak and when we have seen Oaks fail in the past, the layer lines have separated before the screws from the print. • Assembly complexity: • Simple and can be done with build event materials.
2 | • Consumables: • None • Strength: • Limited. The layer lines or weak points of the snap fit can break. Since this is a heavy duty application and print qualities can vary between makers, there is no guarantee these will last over time. • Assembly complexity: • Very simple with no tools.
3 | • Consumables: • Non common hardware. Bolt and Nut.

## DESIGN RATIONALE

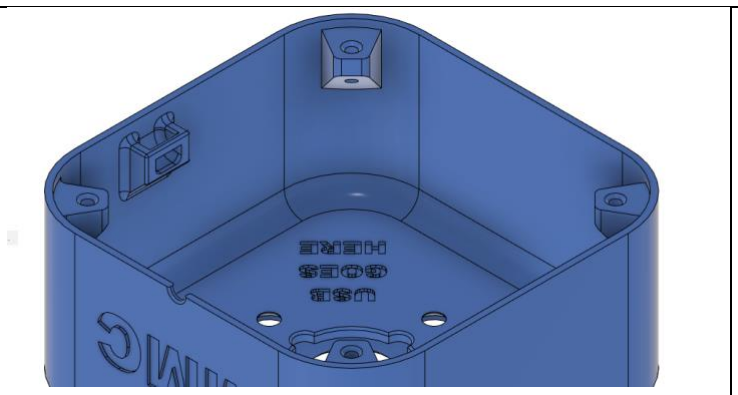
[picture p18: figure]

Files available at <Replace with MMC Library Link> | Page 30 of 43
- Strength:
- Strongest of the 3 options with a metal to metal fastener connection.
- Assembly complexity:
- Creating nut catches on a overhang component could be challenging for most novice 3D printers.
- Getting the nut into the catch without breaking the overhand component could be difficult.

Option 1 was chosen with the rationale that the print lines will fail before the #4 screws are pulled out of the base. This was not calculated, however from the 1 year+ run of the Oak we have not had a user do this yet. When the user is too strong for the use of the oak, the internal component of the Oak or the print lines fail first.

However, if this decision is incorrect, move towards Option 3 through user testing.

Choosing a fastener
- Decision was made to stick with the common part from the Oak (#4 Pan Head Sheet Metal Screw Phillips Drive) because those are commonly available on Digi key, amazon, and already stocked in our offices.

Screw insert features
4 screw inserts were added with the same geometry seen in the Oak joystick.

These have a 45 degree draft to allow them to be printed without support. This and the fillets added were test printed with no issues.

Originally, the location of these features would be in the 4 corners. I learned later this would interfere with the USB of the joystick.

The final design a was set to 4 mm away from the rounded corners of the joystick design. This was so the fillets on these features will have room.

## DESIGN RATIONALE

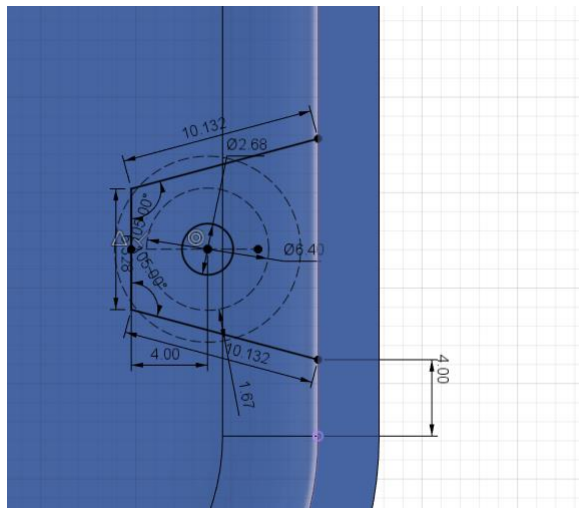
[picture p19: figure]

Files available at <Replace with MMC Library Link> | Page 31 of 43

### Bottom Enclosure

Wall Thickness
3.2 mm – Same reasoning as top enclosure.

Enclosure dimensions
- Matching top enclosure.
- Clearance of bottom of 2 mm since the ¼-20 nut catch has a height of 3.8 mm.

Attachment to Top Enclosure
This feature was heavily inspired by the Oak design as it uses the same attachment mechanism and screw size. The distance between where the head of the screw will be when inserted and beginning of threads on the top enclosure is 3.85 mm (same as oak).

The depth of the screw hole was 10 mm to make contact with the screw holes on the top enclosure

## DESIGN RATIONALE

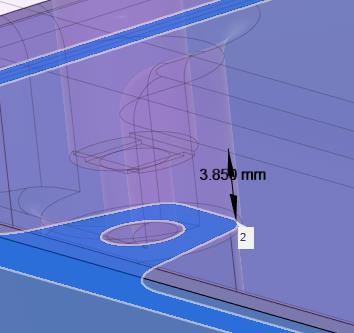
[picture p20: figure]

Files available at <Replace with MMC Library Link> | Page 32 of 43

Extrusions were needed to create a guided path and resistance for the #4 screw to travel and attach. These were created with supporting material surrounding and attaching to the side walls for increased support.

Since this will be an unsupported hole and as such extra layers were added. See the referenced best practices here: https://www.hydraresearch3d.com/design-rules

## DESIGN RATIONALE

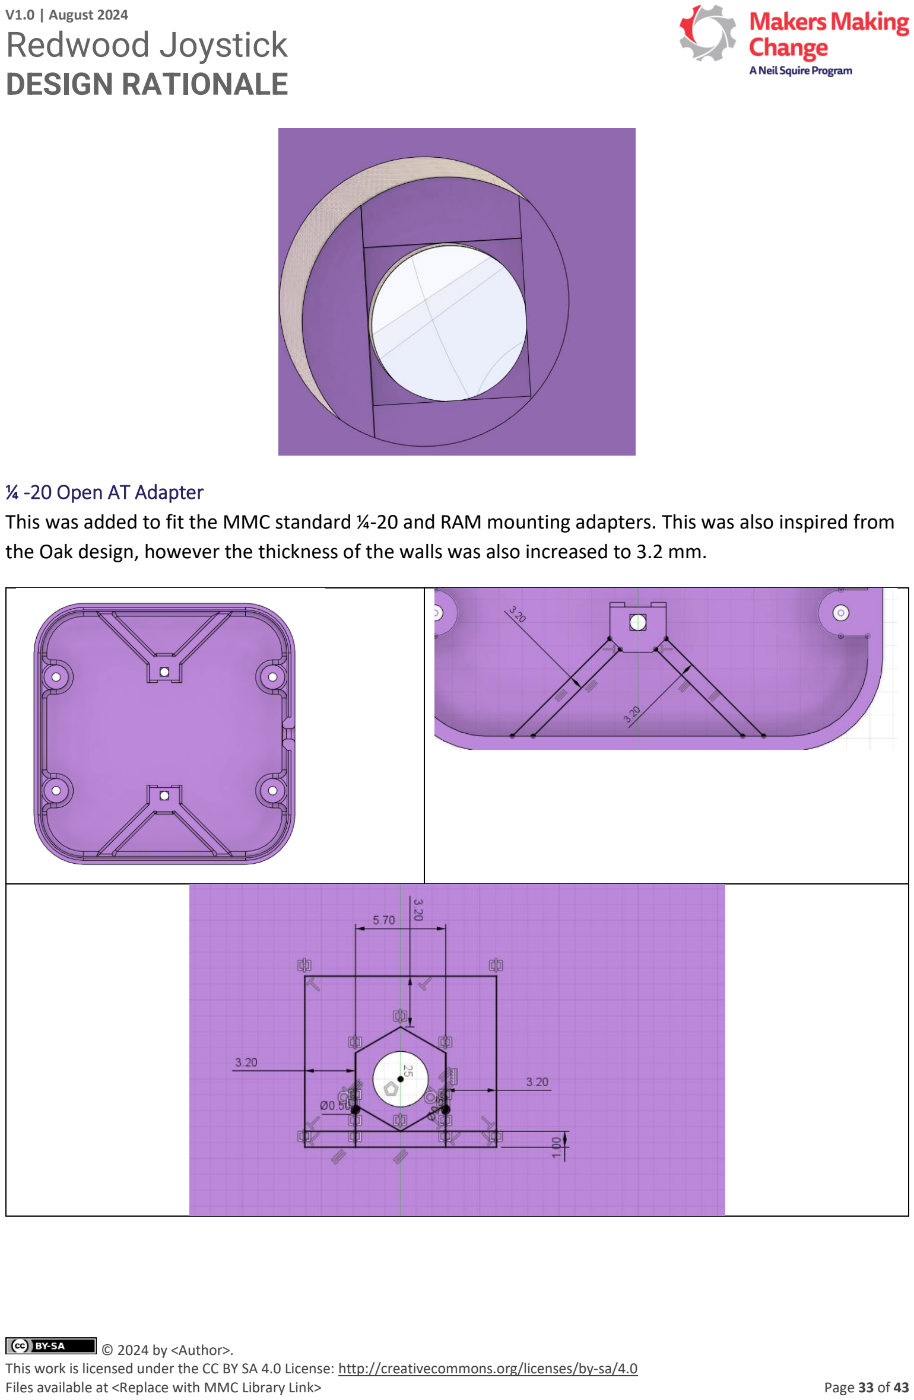
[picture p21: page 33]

Files available at <Replace with MMC Library Link> | Page 33 of 43

¼ -20 Open AT Adapter
This was added to fit the MMC standard ¼-20 and RAM mounting adapters. This was also inspired from the Oak design, however the thickness of the walls was also increased to 3.2 mm.

## DESIGN RATIONALE

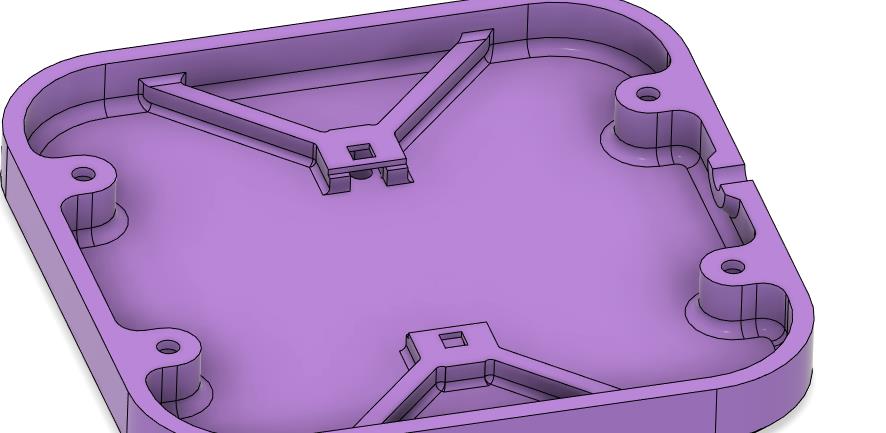
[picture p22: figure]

Files available at <Replace with MMC Library Link> | Page 34 of 43

Inner Fillet
A fillet of 3.5 mm to match curvature of the bottom case.

A fillet of 2 mm was added to reduce strain on joints and support for the screw channels. A 1mm fillet was added to the ¼-20 adapter features.

Alignment to Top Enclosure
When extruding the channels and supports for the #4 screw to pass through, they protrude out of the bottom enclosure. By 0.25mm to reach the screw holes on the top enclosure. Fillets were added to this extension.

## DESIGN RATIONALE

Files available at <Replace with MMC Library Link> | Page 35 of 43

Placement of the top to bottom mounting holes
These mounting holes extruding from the corners of the enclosure with these dimensions of the body (95.5x95.5x56.35 mm (without stick)) will not work with the room needed for the USB to attach as can be seen in the photo below.

Therefore, the options are:

## DESIGN RATIONALE

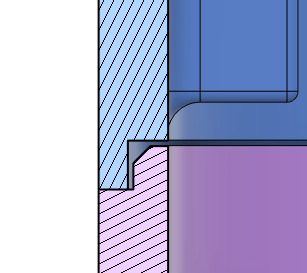
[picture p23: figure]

Files available at <Replace with MMC Library Link> | Page 36 of 43
1. Move the mounting holes
a. This will keep the joystick enclosure small
b. Could result in strength issues. Further testing would be needed to see how much.
2. Increase enclosure length and width to accommodate
a. Would increase dimensions significantly

Decision was made to move the mounting holes and slightly increase width and length to accommodate the cable. The final dimensions are 105.5x105.5x54.7 mm and the mounting holes were added to the side walls.

Shadow line
Adding a shadow line with 0.25 mm clearance for top and side alignment. This helps the esthetics and alignment of the case.

### Optimizing Overall dimensions

Can we make the enclosure smaller as there is quite a bit of extra room on the width and length?

## DESIGN RATIONALE

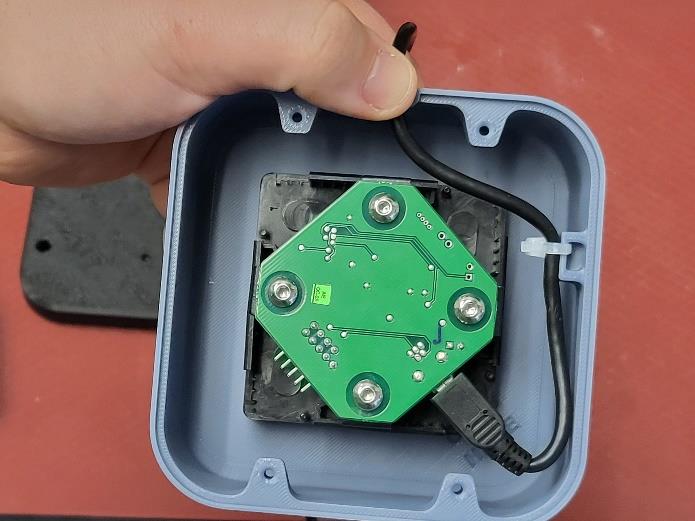
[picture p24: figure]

Files available at <Replace with MMC Library Link> | Page 37 of 43

No, because of the room needed for the USB cable to be attached to the Ultrastik. The current dimensions are as small as the housing can be in this design. It is desirable to give more room as to not cause damage to the USB cable and in case the USB cable source changes.

### Topper connection

- Design discussed in the Conceptual design - Concept 1 proved to work well during testing. Therefore, the only improvement that needs to be made to that design is a way to insert the M6 nut so there is no vertical translation when installing.
- This was done by adding a 3D print disk that is fit in place by a slot locking mechanism. The disk is slid in to the top of the topper nut after the M6 Nut and lined up with the 4 nubs on the inside. The disk then has a rectangular slot that a small coin or flat head screwdriver can turn to lock the nut in place.
- The disk also has a 7 mm hole in the middle so the M6 bolt can pass through with no interference.

## DESIGN RATIONALE

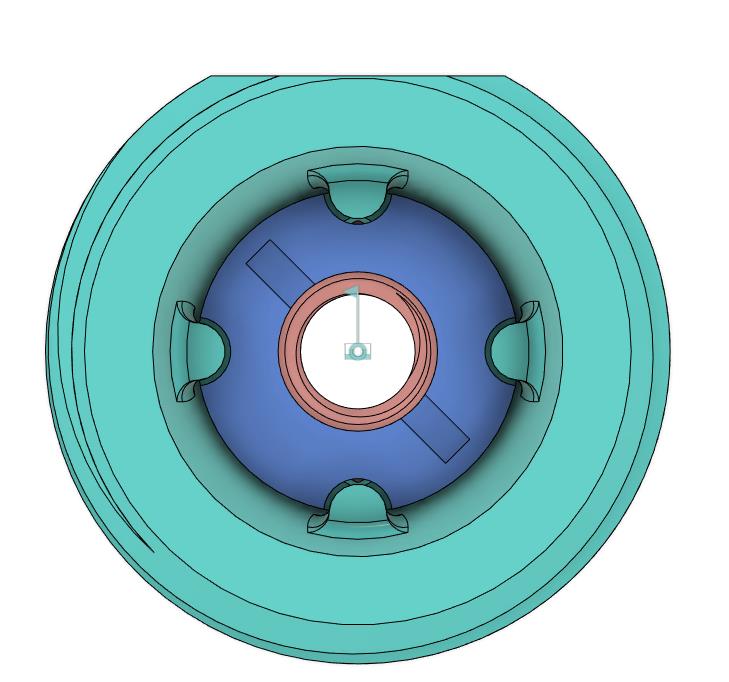
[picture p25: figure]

Files available at <Replace with MMC Library Link> | Page 38 of 43

This was print tested and the nub that had a direct overhang failed. Therefore, that nub was removed on both the disk and topper nut.

## DESIGN RATIONALE

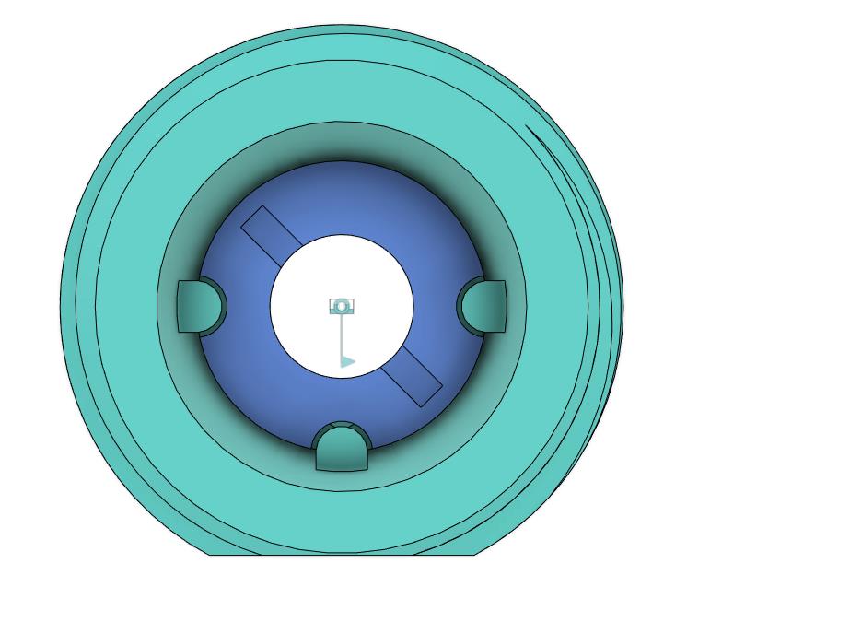
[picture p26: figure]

Files available at <Replace with MMC Library Link> | Page 39 of 43

Other options
A nut catch could have been added to the topper nut (similar to the features seen for the ¼-20 base). This was decided against as this is already a complex part and makers with less reliable/calibrated printers may have difficulty printing it. Also, the disk is not necessary to get the part to screw on. This is more of an assembly aid for those that may have difficulty holding the nut at the same time as threading.

### Comparison to SCCR Model

- SCCR: 109 x 91 x 59.5 mm
- MMC: 105.5x105.5x58.7 mm (without stick)

## DESIGN RATIONALE


Files available at <Replace with MMC Library Link> | Page 40 of 43

### Opportunities for Improvement

- Custom dust covers
- Ensuring correct orientation when assembling

### Design Validation

Aim of this section is to verify the requirements set by the design, user/maker validation, and any other validation required.

### Requirement Validation

Below are the goals, functional, and non-functional requirements from above. A column was added to evaluate if they were met or not.

Goals
| | Was this met? (Y/N)
G01 | Act as a larger and durable form factor for our joystick line. | Y
G02 | Provide an option for users who are breaking the internals of the Oak Joystick. | Y

## DESIGN RATIONALE

Files available at <Replace with MMC Library Link> | Page 41 of 43
G03 | Maker manufacturable in quantities of one. | Y
G04 | The use of support material in 3d printed components should be minimized. | Y
G05 | The number of different filament types should be minimized. | Y
G07 | Material costs should be minimized as to provide a low cost options (Less than or equal to $100 CAD) | Y

Functional Requirements
| | Was this met? (Y/N)
F01 | The joystick shall be usable from a the distance given by the USB cable supplied by UltraStik | Y
F02 | The joysticks shall be compatible with the Xbox Adaptive Controller. | Y
F03 | Joysticks shall be PC compatible. | Y
F04 | The joystick shall denote use orientation. | Y
F05 | The joystick shall have a range of easily interchangeable toppers. | Y
F06 | Toppers shall not interfere with the regular physical motion of the joystick. | Y
F07 | Toppers shall have a secure connection to the joystick. | Y
F08 | The joystick shall be designed to be used by either hand. | Y
F09 | Joystick shall remain stable when in use. | Y
F10 | The housing shall protect internal components from outside sources. | Y
F11 | Joystick designs shall support camera mounting styles. | Y
F12 | Joystick designs shall support hook and loop fastener mounting styles. | Y
F13 | Joystick designs shall support tabletop mounting styles with no fasteners. | Y
F14 | Enclosure shall work with the Ultrastik joystick component | Y

Non-functional Requirement
| | Was this met? (Y/N)
NF01 | Documentation should be maintainable with the use of commonly available software. | Y
NF02 | Documentation must be available in a digital format. | Y
NF03 | Documentation must be printable. | Y
NF04 | Documentation, code, and hardware must have appropriate open-source licenses. | Y
NF05 | Instructions must be provided for using joystick with XAC for gaming | Y
NF06 | Instructions must be provided for using joystick with PC/Phone/Tablet for gaming | Y
NF07 | Instructions must be provided for using joystick with PC/Phone/Tablet for digital access | Y

### User/Maker Validation

Foothills
- Sent to Foothills at Dec 6

th, 2024
- First impressions feedback
- “It is great to have a larger size joystick that is more durable”
- “I have a client that I am seeing this will be perfect for”

## DESIGN RATIONALE

Files available at <Replace with MMC Library Link> | Page 42 of 43
- “The joystick spinning will be challenging for the toppers that need to be aligned a certain way for the user”
- The center will then keep the joystick and provide feedback once they work with gamers who it is suited for

User 1
- User 1 has a modified version of the Oak called the Mighty Oak as their unit was failing at the print lines with the regular Oak. He was interested in trialing the Redwood Joystick as an alternative.
- Joystick will be sent to him late Dec 2024 for testing.

Josie
- Josie is the only other MMC team currently with an Ultrastik Joystick. She has print tested and assembled the joystick with the following feedback on the design:
- Joystick assembled easily and as expected.
- Works with XAC as expected.
- Works on PC as expected.
- In analog mode, drifts on IOS device. In mouse mode works fine.

### Update – v1.1

The ball topper version of the joystick was out of stock for a while so we created an alternate version that works with the oval topper version.

The enclosure is the same but the thread for the topper is a M10 not an M6. Therefore, a new topper nut was designed. This was just created to have an insert for a M10 nut without the catch.

## DESIGN RATIONALE

Files available at <Replace with MMC Library Link> | Page 43 of 43

### Appendix A – Option of using a base with spacers already imbedded

This approach was explored and was abandoned. The thoughts around what hardware to use was archived in this appendix.

### Choosing the size of the faster

With a spacer design and not having a M5 machine screw already in our common parts, we have flexibility to choose a commonly available and lowest cost M5 machine screw length.

The common build event tools do not include any hex type drivers. With this, only Philips or slotted heads were considered.

Fastener | Cost for 4 (CAD) | Availability/source | Notes
M5X10 – Philips | 13.15 | DigiKey – 200 in stock | Only come in pack of 100
M5x12 – Philips | 13.15 | DigiKey – 200 in stock | Only come in pack of 100
M5x8 - Philips | 9.19 | Amazon – only 8 left in stock | Pack of 20
M5x10 – Philips | 12.89 | Amazon – only 3 left in stock | Pack of 50
Hardware store (home depot)

*Note that the stock was estimated as of Nov 13, 2024

With this, decide on M5X10.

Spacer integrated
- Should the tunnel part be a cylinder? Would another shape print better?
- Are the screw drivers in the build kits long enough?
- Add some type of key for orientation so the cable comes out the right side
- Unsupported hole

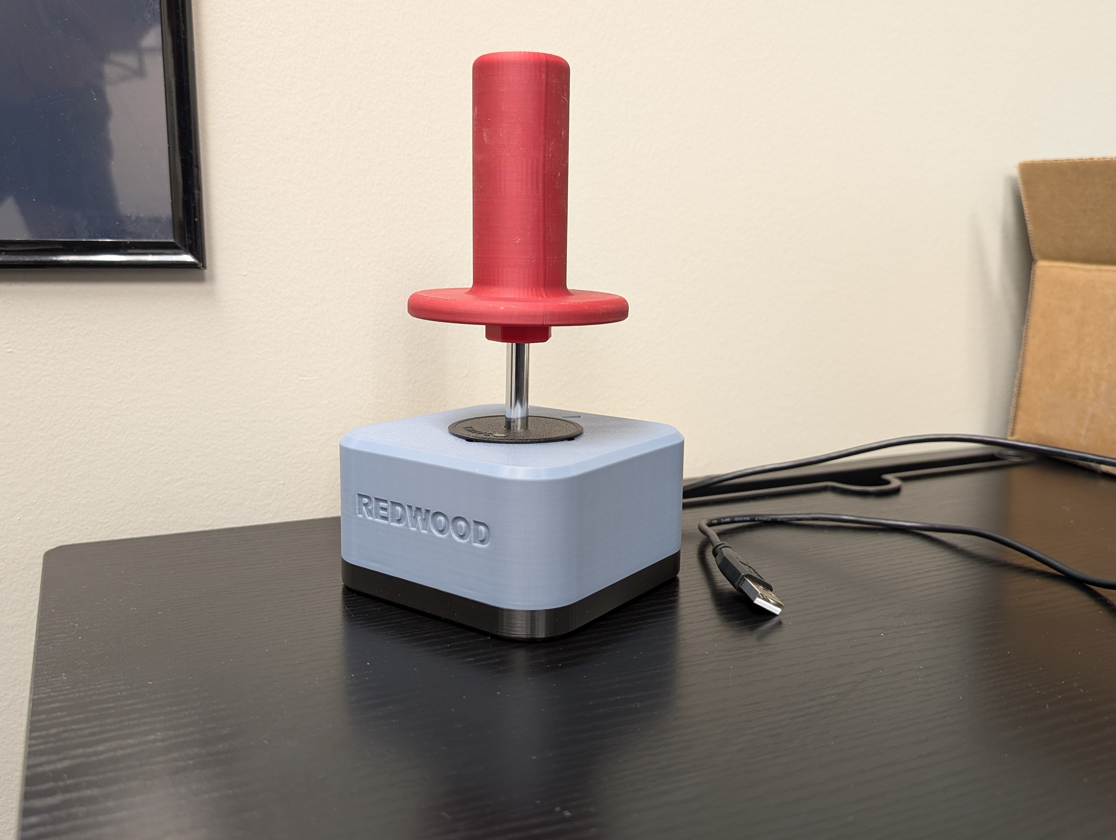
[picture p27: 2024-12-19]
Photos/Redwood-with-stick.jpg

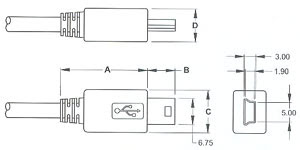
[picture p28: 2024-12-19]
Photos/Reference_Images/usb micro reference.jpg

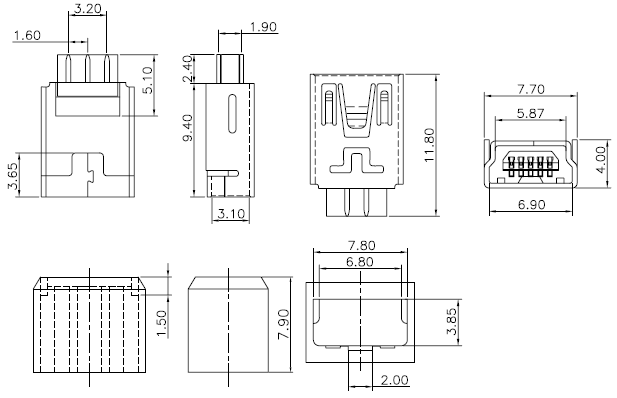
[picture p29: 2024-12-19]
Photos/Reference_Images/mini usb connector ref.png

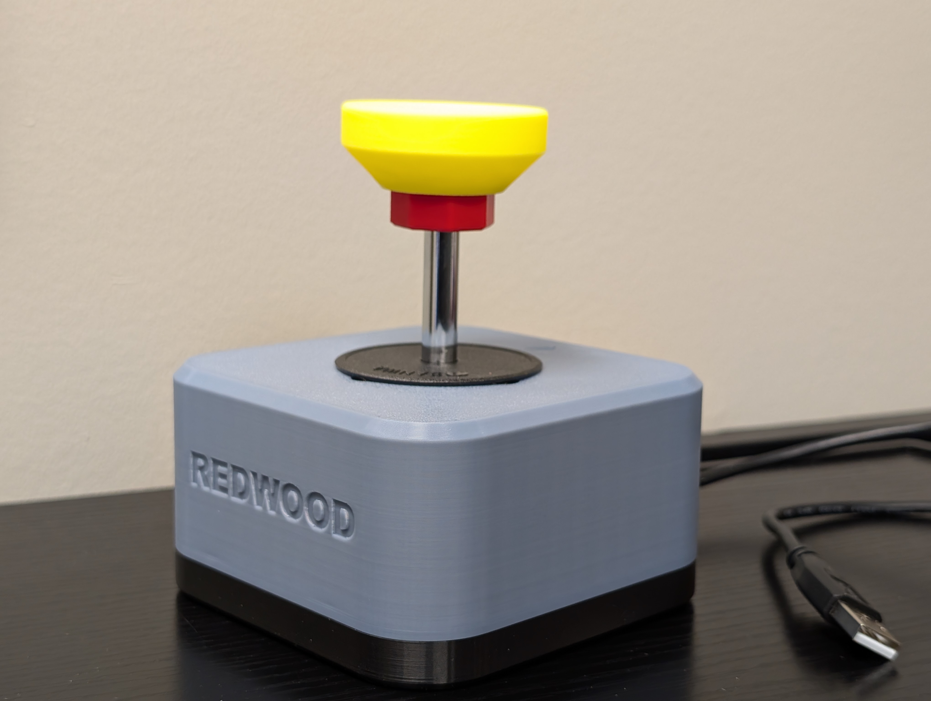
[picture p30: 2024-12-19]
Photos/Redwood-with-cup.jpg

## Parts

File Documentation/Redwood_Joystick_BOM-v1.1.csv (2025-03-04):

Device: | Redwood Joystick
Version: | V1.0
Last Updated: | 2024-12-17
 |  |  |  |  |  |  |  | Total filament (g) |  | Unit Cost | Total Estimated Cost | Build Cost
 |  |  |  |  |  |  |  | 150.34 |  | $94.17 | $97.08
ID | Commercial Parts |  |  |  |  |  |  |  |  | $90.19 | $93.10
 | Part | Description |  | Manufacturer | Supplier | QTY / Device | QTY / PKG | PKGs | $/ PKG | $ / Device | Total Estimated Cost |  | Link
A01 | Screw, #4 self-tapping 3/8" length | For attachment of bottom enclosure to top enclosure. |  | DigiKey | DigiKey | 4 | 1 | 4 | $0.63 | $2.52 | $2.52 |  | https://www.digikey.ca/en/products/detail/serpac/6005/307599
A02 | UltraStik 360 Ball Top (analog) | 59 USD. Estimated CAD cost at 1.4179 conversion rate. You will need to pay customs fees if you are outside of the USA. |  | Ultimarc | Ultimarc | 1 | 1 | 1 | $83.65 | $83.65 | $83.65 |  | https://www.ultimarc.com/arcade-controls/joysticks/ultrastik-360-oval-top-clone/
A03 | Hex nut, M3 | Included incase a mounting adapter is used |  | DigiKey | DigiKey | 2 | 1 | 1 | $0.27 | $0.54 | $0.27 |  | https://www.digikey.ca/en/products/detail/keystone-electronics/4708/4499301
A04 | Cable tie, 4" | Strain Relief |  | DigiKey | DigiKey | 1 | 1 | 1 | $0.17 | $0.17 | $0.17 |  | https://www.digikey.ca/en/products/detail/3m/CT4NT18-M/2721151
Items Below are optional. See Maker Guide
B01 | Metric Hex Nut M6-1.00 | OPTIONAL: IF USING TOPPER ADAPTER |  | Home Depot | Home Depot | 1 | 10 | 1 | $3.97 | $0.40 | $3.97 |  | https://www.homedepot.ca/product/paulin-metric-hex-nut-m6-1-00-10pcs/1001588038
B06 | M3x12mm screw | OPTIONAL: IF USING MOUNTING ADAPTER |  | DigiKey | DigiKey | 2 | 2 | 1 | $1.11 | $1.11 | $1.11 |  | https://www.digikey.ca/en/products/detail/apm-hexseal/RM3X12MM-2701/2063201
B07 | 1/4?-20 UNC Tee Nut Insert, 5/16? Length | OPTIONAL: IF USING CAMERA MOUNTING ADAPTER |  | Home Depot | Home Depot | 1 | 1 | 1 | $0.55 | $0.55 | $0.55 |  | https://www.homedepot.ca/product/paulin-1-4-inch-20-tee-nuts-4-prong-5-16-inch-barrel-length/1000129429
 | 1/4?-20 Bolt (any length greater than 10 mm) | OPTIONAL: IF USING CAMERA MOUNTING ADAPTER |  | Home Depot | Home Depot | 1 | 1 | 1 | $0.86 | $0.86 | $0.86 |  | https://www.homedepot.ca/product/paulin-1-4-20-x-1-inch-hex-head-cap-screw-18-8-stainless-steel-unc/1000142352
B08 | Metric Hex Nut M10 | ALTERNATE: ONLY IF USING "UltraStik 360 Oval Top" |  | Home Depot | Home Depot | 1 | 10 | 1 | $3.97 | $0.40 | $3.97 |  | https://www.homedepot.ca/product/paulin-m10-1-50-class-8-metric-hex-nut-din-934-zinc-plated/1000128523
 | 3D Printed Parts |  |  |  |  |  |  | 164.02 |  | $3.98 | $3.98
 | Part | Description | Filament Type | Filament | Color | QTY / Device | Mass (g) / Part | Total Mass | $ / kg | $ / Device | Total Estimated Cost |  | Link
A05 | Redwood-Enclosure-Base-v1.0 | Printed with 4 wall loops | PLA |  | Any | 1 | 46.15 | 46.15 | $25.00 | $1.15 | $1.15
A06 | Redwood-Enclosure-Top-v1.0 | Printed with 4 wall loops | PLA |  | Any | 1 | 92.63 | 92.63 | $25.00 | $2.32 | $2.32
Items Below are optional. See Maker Guide
B02 | Redwood-Topper-Adapter-Nut-v1.0 | OPTIONAL: IF USING TOPPER ADAPTER | PLA |  | Any | 1 | 4.87 | 4.87 | $25.00 | $0.12 | $0.12
B03 | Redwood-Topper-Adapter-Cover-v1.0 | OPTIONAL: IF USING TOPPER ADAPTER | PLA |  | Any | 1 | 0.34 | 0.34 | $25.00 | $0.01 | $0.01
B04 | RAM Mounting Adapter | OPTIONAL: IF USING RAM MOUNTING ARM | PLA |  | Any | 1 | 6.35 | 6.35 | $25.00 | $0.16 | $0.16
 | Camera Mount Adapter | OPTIONAL: IF USING 1/4-20 MOUNTING ARM | PLA |  | Any | 1 | 8.81 | 8.81 | $25.00 | $0.22 | $0.22
B05 | Redwood-Joystick-Topper-Adapter-OvalTopper-v1.0 | ALTERNATE: ONLY IF USING "UltraStik 360 Oval Top" | PLA |  | Any | 1 | 4.87 | 4.87 | $25.00 | $0.12 | $0.12
 | Tools
 | Tool | Description |  | Manufacturer | Supplier |  |  |  |  |  |  |  | Link
T01 | Philips screw driver
T02 | 3D printer
T03 | Canadian dime (helps spin the adapter cover)
T04 | Flush Cutters
 | Alternatives
 | Part | Description |  | Manufacturer | Supplier | QTY / Device | QTY / PKG | PKGs | $/ PKG | $ / Device | Total Estimated Cost |  | Link
 | UltraStik 360 Oval Top (analog) | If the ball topper is out of stock you can use the Oval version. The topper adapter nut will NOT work with this model, you will have to print the alternate version found in the build files. |  | Ultimarc | Ultimarc | 1 | 1 | 1 | 83.65 | 83.65 | 83.65 |  | https://www.ultimarc.com/arcade-controls/joysticks/ultrastik-360-oval-top-en-2/

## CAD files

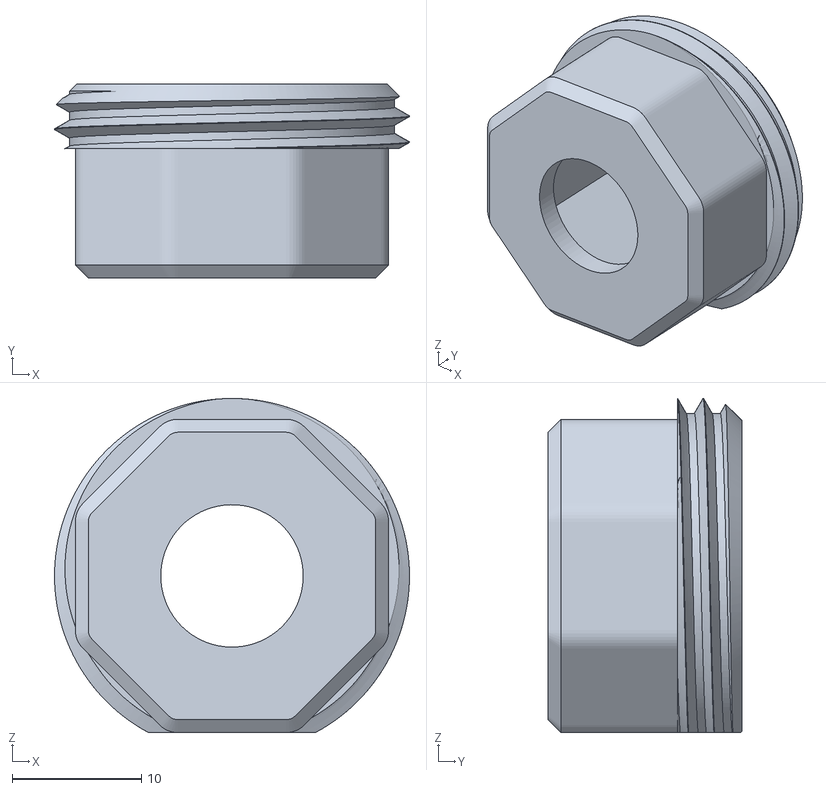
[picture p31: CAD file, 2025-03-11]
Build_Files/3D_Printing_Files/Alternate-Parts/Redwood-Joystick-Topper-Adapter-OvalTopper-v1.1.stl
27.4 x 15.0 x 25.8

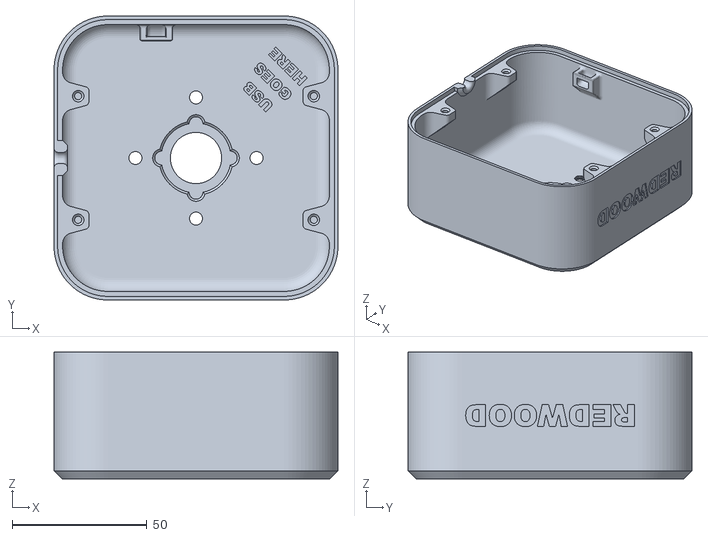
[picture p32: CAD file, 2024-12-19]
Build_Files/3D_Printing_Files/Redwood-Joystick-Enclosure-Top-v1.0.stl
105.5 x 105.5 x 47.1

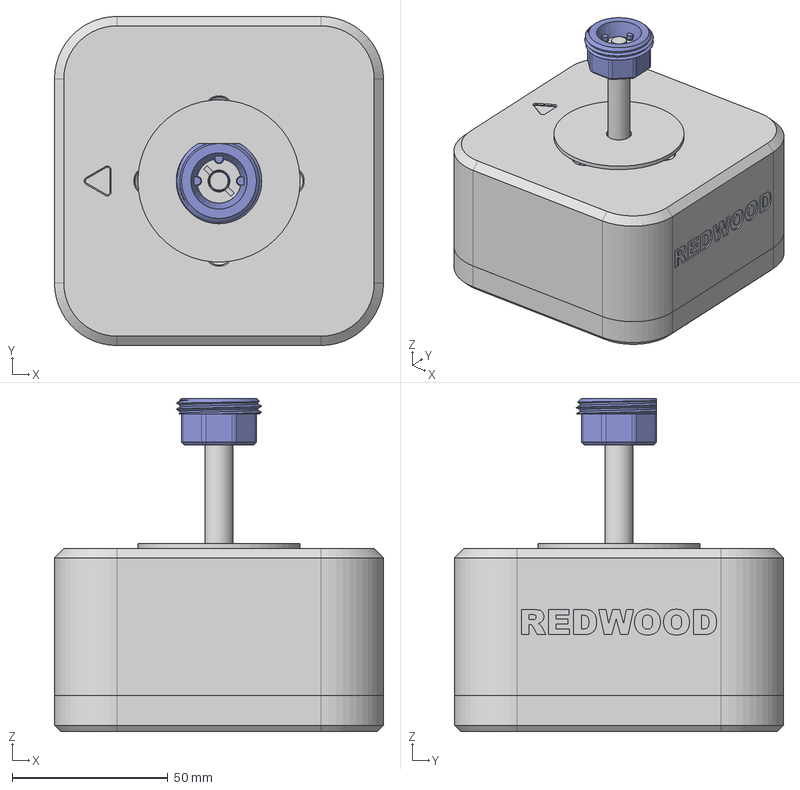
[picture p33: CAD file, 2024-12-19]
Design_Files/CAD_Design_Files/Step/Redwood-Joystick-v1.0.step
105.5 x 105.5 x 106.9 mm
Enclosure Top
Enclosure Bottom
Cable
Dust Cover
Topper_nut
M6 Nut v3 v1
Nut-Cover

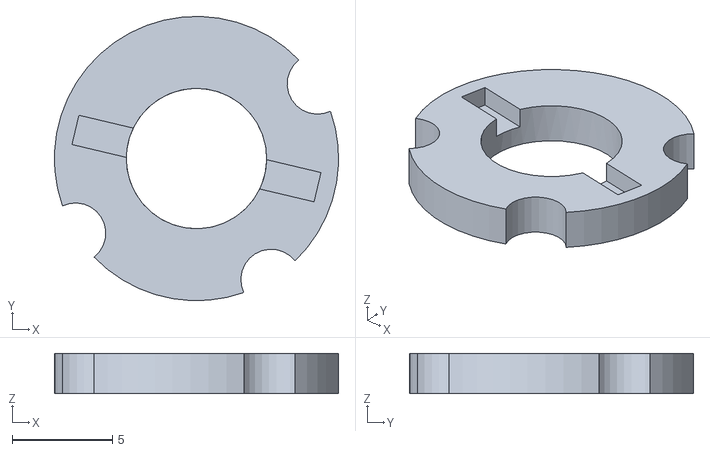
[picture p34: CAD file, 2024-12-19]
Build_Files/3D_Printing_Files/Redwood-Joystick-Topper-Adapter-Cover-v1.0.stl
14.2 x 14.2 x 2.00

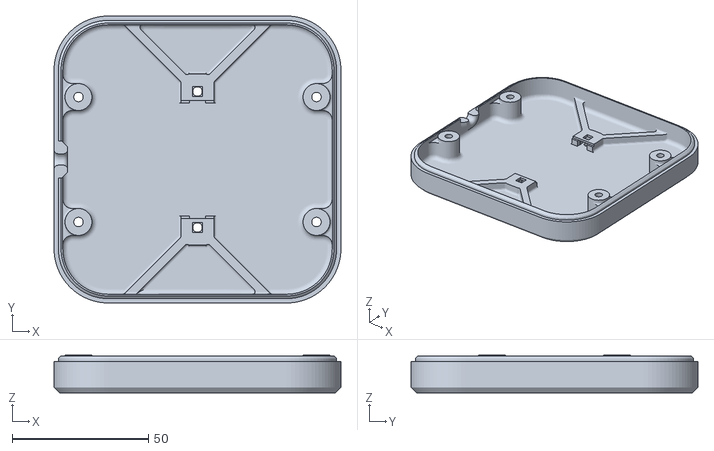
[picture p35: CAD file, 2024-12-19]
Build_Files/3D_Printing_Files/Redwood-Joystick-Enclosure-Base-v1.0.stl
105.5 x 105.5 x 13.9

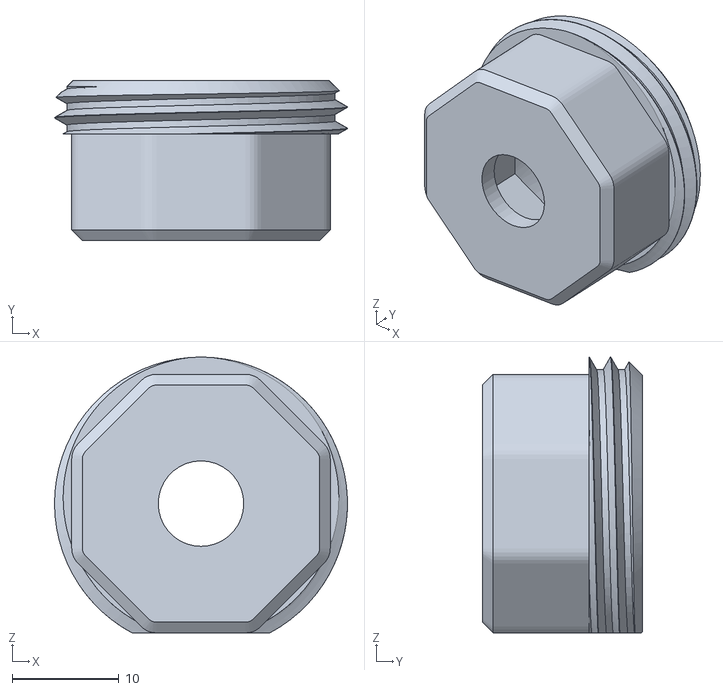
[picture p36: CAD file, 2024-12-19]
Build_Files/3D_Printing_Files/Redwood-Joystick-Topper-Adapter-Nut-v1.0.stl
27.4 x 15.0 x 25.8

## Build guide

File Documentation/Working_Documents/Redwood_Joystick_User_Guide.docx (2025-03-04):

# Overview

This document contains the necessary information to use the Redwood Joystick, a robust analog USB joystick that can be used for digital access or adaptive gaming. This design is based off of Ultimarc’s UltraStik 360 joystick (https://www.ultimarc.com/arcade-controls/joysticks/ultrastik-360-oval-top-clone/) and 3D printed enclosure and various toppers have been added to this design.

Isometric view of the Redwood joystick with a glossy black ball topper. A USB type A cable can be seen on the side. Top enclosure is light blue and base is black.

## Introduction

The Redwood Joystick is a robust analog USB joystick that can be used for digital access or adaptive gaming. The Redwood was designed for users with gross motor movement and high strength that other joysticks may not be able to withstand.

## Features

The Redwood Joystick uses the Ultimarc Ultrastik Joystick as the main internal component. This comes with a default ball topper. If you need other toppers such as goalpost, concave, stick, etc. the Topper Adapter Nut can be used to attach our Oak Joystick toppers. Using the mounting adapters you can mount the joystick on RAM or ¼-20 camera mounts.

Number | Feature | Functionality
1 | Ultimarc Ball topper | Default topper that comes with the joystick.
2 | Ultimarc Dust Cover | Prevents dust and grime to enter the inside of the enclosure.
3 | USB Type-A | Allows for connection to devices.
4 | Oak Joystick Toppers | Any of the Oak Joystick toppers will fit the Redwood Joystick using the Topper Adapter Nut. See all small, medium, and large Oak toppers here: https://tinyurl.com/OakTopper
5 | Topper Adapter Nut | Adapter that allows any Oak Joystick topper to fit the Redwood Joystick.
6 | 1 inch RAM Mount Adapter | Can be attached to the bottom of the Redwood Joystick to attach to 1 inch (Type B) RAM mounts.
7 | Camera Mount Adapter | Can be attached to bottom of Redwood Joystick to attach to ¼-20 mounting (common camera mount)

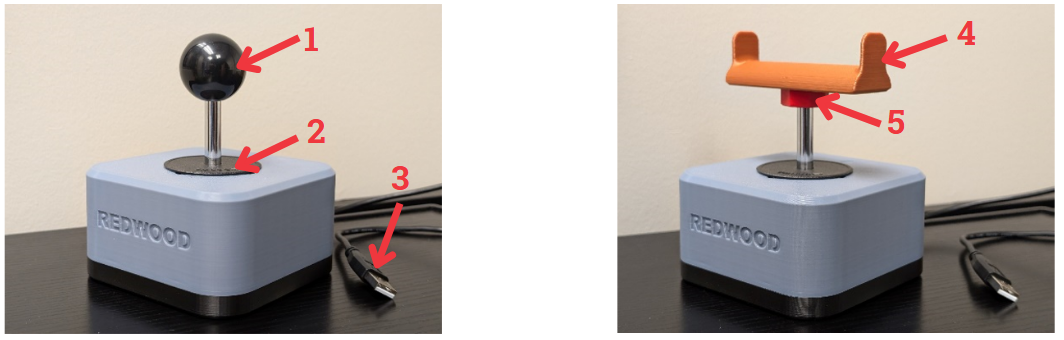
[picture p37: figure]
labeled diagram of the parts of the redwood. One has the default black glossy ball topper and the other has a 3D printed goalpost topper.
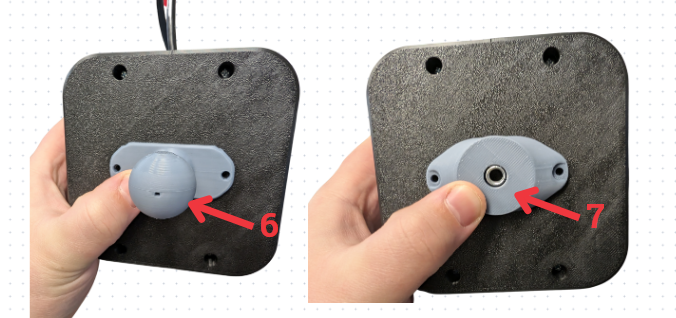
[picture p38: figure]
two photos of the bottom of the redwood joystick. One with a camera mount adapter and one with the RAM mount adapter.

### Oak Toppers

To add any of the Oak toppers, screw on the Topper Adapter Nut to the threads on the stick until secure. Then thread on the Oak topper of your choice.

The Oak Joystick toppers come in a standard small, medium, and large size and can be customized by the maker. There is a stick, goalpost, ball, concave, and convex topper. These are all compatible with the Redwood Joystick using the Topper Adapter Nut. If you are wanting to evaluate the size of the toppers, please see the Oak Joystick Topper Guide: https://github.com/makersmakingchange/Oak-Compact-Joystick/blob/main/Documentation/Oak_Joystick_Topper_Guide.pdf

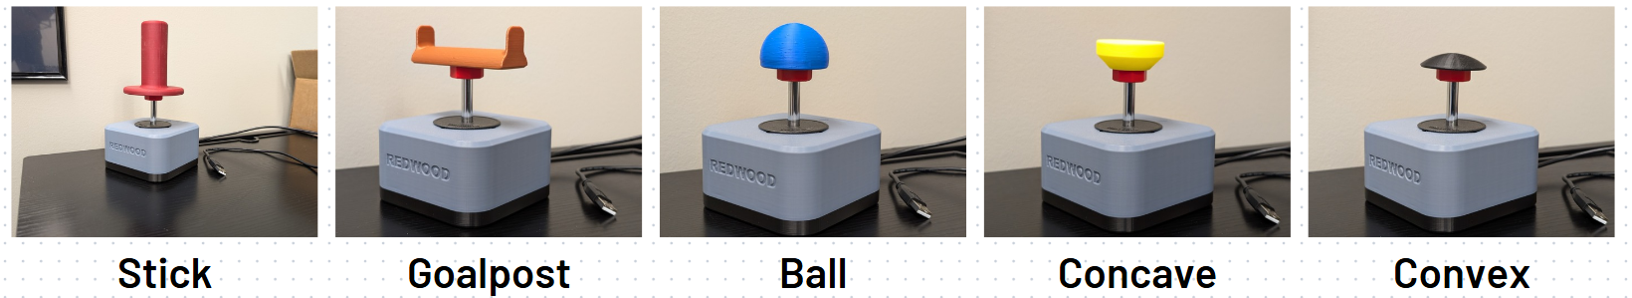
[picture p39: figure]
5 photos of the different toppers on the redwood joystick. in order from left to right, stick, goalpost, ball, concave, convex.

## Specifications

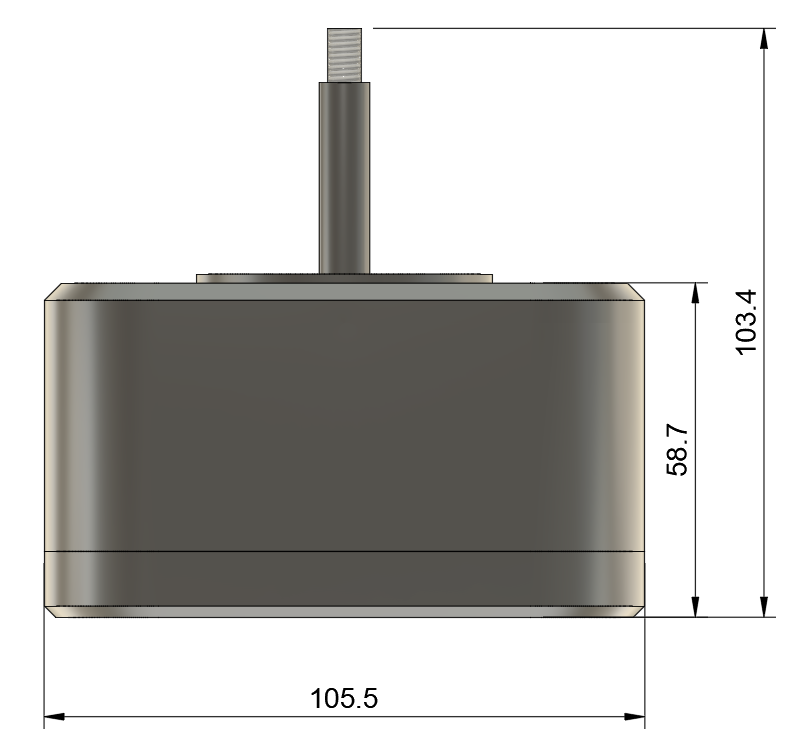
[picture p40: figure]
rendering of the redwood joystick with dimensions. showing the total height with the stick to be 103.4 mm and without 58.7 mm and the width of the device 105.5 mm.

Item | Redwood Joystick
Size (Length x Width x Height) [mm] | 105.5 x 105.5 x 58.7 (not including height of stick) 105.5 x 105.5 x 103.4 (Including height of stick)
Mass [g] | 274
Type of Cable | USB Type-A
Operating Force (grams) | 298
Range of Motion (degrees) | ±15.5°

## Compatibility

More testing is required to see if the joystick will work on macOS.

Item | Redwood Joystick
PC (Windows XP or Newer) | Yes
macOS | Unknown
IOS | Yes, however only in mouse mode. Using the default analog mode will cause drift. See section below on how to change to mouse mode.
Android (Oreo or newer) | Yes
Xbox Adaptive Controller | Yes
Sony Access Controller | No (Sony Access Controller does not have USB port)
Hori Flex Controller | Yes

## Usage

Connect the Redwood Joystick to your device using the provided USB cable. You may need an adapter or dongle to get the USB connected to your system. The Joystick is by default in Analog Gamepad mode. This means it will act as a joystick for a gamepad system. You can change the mode it is in by using the UltraMap application created by Ultimarc. See the modes available below. Download the software here: https://www.ultimarc.com/arcade-controls/joysticks/ultrastik-360-oval-top-clone/

### UltraMap – Mode Selection

By default, the Redwood Joystick will be in Analog mode. The UltraMap application allows you to program the joystick in the following modes:

Mode | Description
2-Way, Up & Down | The joystick restricts movement to only two directions: up and down.
4-Way | Movement is limited to the four cardinal directions: up, down, left, and right.
4-Way, Diagonals Only | Movement is restricted to diagonal directions (e.g., up-right, up-left, down-right, down-left).
8-Way | Full freedom of movement in eight directions: up, down, left, right, and all four diagonals.
8-Way, Easy Diagonals | Similar to 8-Way but optimized for smoother diagonal inputs, reducing the effort required to hit diagonal positions accurately.
Analog | Behaves like a gamepad joystick with proportional controls.
Mouse Pointer | Behaves like a USB mouse pointer. No left or right click buttons included.

To change modes, download the UltraMap application to a computer and plug in the Redwood Joystick. Scan for Ultrastik Joysicks and then select the mapping you want under the “Joystick Map” drop down. Then click the download button and wait for the mode to change. Then, the joystick will behave in that mode across all devices until you upload a different mode to it. See the Ultrastik installation instructions for more details: https://www.ultimarc.com/arcade-controls/joysticks/ultrastik-360-oval-top-clone/

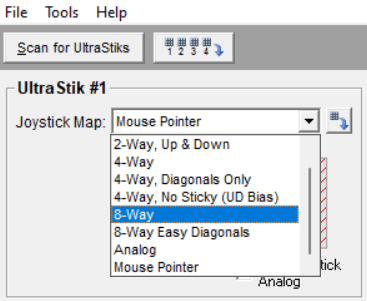
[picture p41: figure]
Screenshot of the Ultimarc app. Showing the drop down menu of the modes the joystick can be put in.

### Takedown / Storage

When not in use, the Redwood Joystick should be stored in a cool place out of direct sunlight.

### Customization

Ultimarc offers an optional “Hard Spring”. Purchasing this spring and swapping it out with the spring inside of the joystick will result in a higher force needed to operate. Link to the Hard Spring can be found here: https://www.ultimarc.com/arcade-controls/joystick-accessories/ultrastik-360-optional-hard-spring/

## Care

The Redwood Joystick is made of 3D printed plastic. Exposure to high heat may cause warping and/or negatively affect function. Extended exposure to sunlight will also weaken the plastic on the device.

The Redwood Joystick contains electronics and is not waterproof. If the device becomes wet, make sure it is off and do not use it until it has completely dried. It may help to open any electronic enclosures to speed up drying and ensure it has completely dried.

### Cleaning

The Redwood Joystick can be wiped with a damp cloth. The Redwood Joystick can also be cleaned by scrubbing with warm water and dish soap. Do not use hot water or clean in a dishwasher.

If using warm water and dish soap, ensure any electronic components have been removed before washing.

## Disposal

PLA filament may be industrially compostable in your area. Check with your waste management company if PLA can be composted or must be thrown in the garbage.

Disassemble the Redwood Joystick and separate out the recyclable and compostable components, and those that must be thrown out. Electronics and batteries should be disposed of following your local waste management guidelines.

© 2024 by Neil Squire. This work is licensed under the CC BY SA 4.0 License: http://creativecommons.org/licenses/by-sa/4.0 Files available at https://github.com/makersmakingchange/Redwood_Joystick/tree/main Page 2 of 3

V1.0 | Dec 2024 Redwood Joystick user Guide

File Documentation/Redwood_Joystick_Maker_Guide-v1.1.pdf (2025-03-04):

V1.0 | Dec 2024

## Redwood Joystick

## MAKER GUIDE

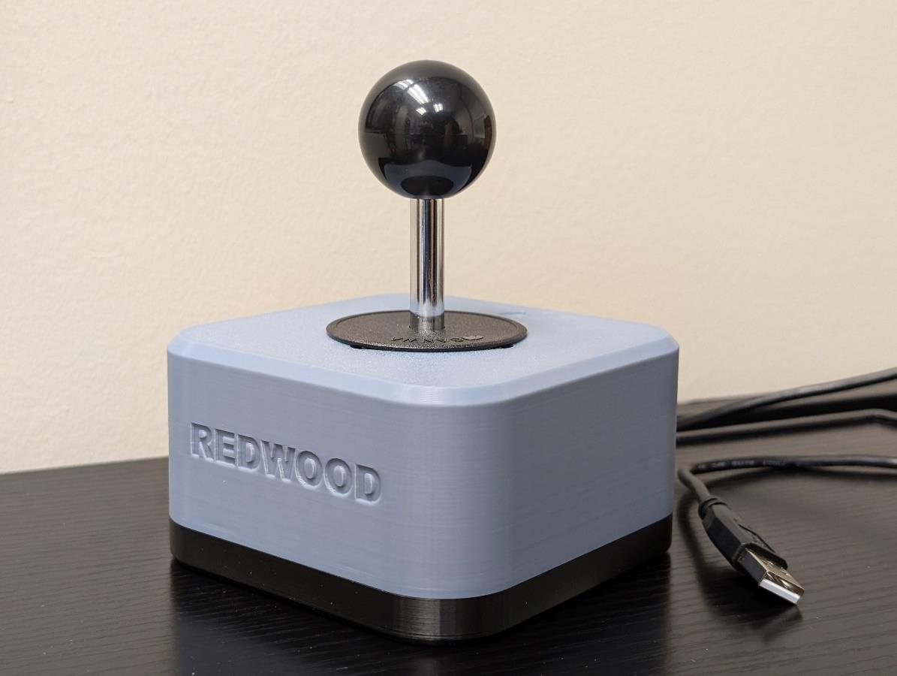
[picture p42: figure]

© 2024 by Neil Squire. (https://neilsquire.ca/)
This work is licensed under the CC BY SA 4.0 License: http://creativecommons.org/licenses/by-sa/4.0
Files available at https://github.com/makersmakingchange/Redwood_Joystick/tree/main | Page 1 of 23

### Overview

This document contains the necessary information to build the Redwood Joystick, a robust analog USB joystick that can be used for digital access or adaptive gaming. The Maker Checklist outlines the required steps, including questions for the User. The Tool List contains a comprehensive list of tools and supplies required to complete the build. The 3D Printing Guide contains print settings and quantities for the 3d printed components. The Assembly Guide contains all the necessary steps to assemble and program the device. Finally, the Testing Guide contains a set of tests to confirm the Redwood Joystick works properly.

## MAKER GUIDE

Files available at https://github.com/makersmakingchange/Redwood_Joystick/tree/main | Page 2 of 23

### Contents

Overview | 1
Maker Checklist | 4
Maker To Do List | 4
Items to Give to User | 4
Tool List | 5
Tools / Equipment | 5
Supplies | 5
Personal Protective Equipment (PPE) | 5
Customization Guide | 6
3D Printing Guide | 7
3D Printing Summary | 7
3D Printing Settings | 7
Post-Processing | 7
Maker Component List | 9
Assembly Guide | 10
Part A: Enclosure | 11
Part A: Required Components | 11
Part A: Required Tools and Supplies | 11
Part A: Required Personal Protective Equipment (PPE) | 11
Part A: Enclosure Assembly Steps | 12
Part B: Topper and Mounting Adapters (OPTIONAL) | 18
Part B: Required Components | 18
Part B: Required Tools and Supplies | 18
Part B: Required Personal Protective Equipment (PPE) | 18
Part B: Topper Adapter Assembly Steps | 18
Part C: Mounting Adapters (OPTIONAL) | 19
Part C: Required Components | 20
Part C: Mounting Adapter Steps | 21

## MAKER GUIDE

Files available at https://github.com/makersmakingchange/Redwood_Joystick/tree/main | Page 3 of 23
Testing | 23
Troubleshooting | 23

## MAKER GUIDE

Files available at https://github.com/makersmakingchange/Redwood_Joystick/tree/main | Page 4 of 23

### Maker Checklist

This list provides an overview of the steps required to build and deliver the Redwood Joystick

### Maker To Do List

Read through the Maker Guide to become familiar with required components, tools, supplies, safety gear, and overall assembly steps.
Talk to the User about customization options
- Color of prints:
- Can customize the top and/or bottom enclosure.
- Topper colors can also be customized if toppers are requested.
- Topper sizing:
- The toper adapter allows the Oak Toppers (https://github.com/makersmakingchange/Oak-Compact-Joystick/tree/main/Build_Files/3D_Printing_Files/Toppers) to be compatible. There is a default small, medium, and large size of toppers. There is also a topper sizing guide (https://github.com/makersmakingchange/Oak-Compact-Joystick/blob/main/Documentation/Oak_Joystick_Topper_Guide.pdf) that you can send to the user to see which size and shape they would prefer.
- Mounting options:
- There are RAM and ¼-20 mounting adapters available from the Oak joystick (https://github.com/makersmakingchange/Oak-Compact-Joystick/tree/main/Build_Files/3D_Printing_Files/Toppers) as well that will fit.
- Ask the user which way they would like to mount the joystick.
- Tabletop – ask if hook and loop should be added to the bottom
- Mounting arm – ask if it has a ¼-20 thread or a RAM attachment (confirm it is RAM type B [1-inch] Compatible)
- How they would like to receive the “User Guide” (PDF or physical copy) Order hardware components
Gather tools, supplies, and safety equipment.
Assemble the device
Test the Redwood Joystick
Print “User Guide” (if the User would like a physical copy)

### Items to Give to User

Assembled Redwood Joystick
- Optional:
- Topper adapter if they want to use any Oak toppers.
- Oak toppers they may want.
User Guide

## MAKER GUIDE

Files available at https://github.com/makersmakingchange/Redwood_Joystick/tree/main | Page 5 of 23

### Tool List

### Tools / Equipment

Tool ID | Description | Required / Recommended | Notes
T01 | Philips screw driver | Required | Tighten/loosen Philips head fasteners
T02 | 3D printer | Required | Printing the enclosure/possible toppers and adapters
T03 | Canadian Small Coin (Dime) | Recommended | If using a topper adapter, it helps spin the adapter cover. Any small coin will work.
T04 | Flush Cutters | Recommended | Cutting the cable tie. Scissors or other cutting tools may work.

### Supplies

Supplies ID Description | Quantity | Notes
S01 | Filament | 150g

### Personal Protective Equipment (PPE)

PPE ID | Description | Notes
P01 | Safety Glasses | When cutting the cable tie, wear safety glasses to
prevent debris entering your eyes.

## MAKER GUIDE

Files available at https://github.com/makersmakingchange/Redwood_Joystick/tree/main | Page 6 of 23

### Customization Guide

The device can be printed in the user’s desired colour. As a suggestion, the bottom and top enclosure can be matching or different colors depending on the users preference.

## MAKER GUIDE

Files available at https://github.com/makersmakingchange/Redwood_Joystick/tree/main | Page 7 of 23

### 3D Printing Guide

The device was originally printed on a Bambu P1S using the Bambu Studio slicer.

### 3D Printing Summary

Metrics | Single Unit
Total Print Time (hour min) | 3h 2m
Total Number of Components | 2
Typical Total Mass (g) | 139.01
Typical Number of Print Setups | 1

### 3D Printing Settings

Note that the 3D printing material should be assumed to be PLA unless otherwise noted in the table below.

Print File Name | Qty | Total Print Time (hr:min) | Mass (g) | Infill (%) | Support(Y/N) | Layer Height/ Nozzle Diameter(mm) | Notes
Redwood-Joystick-Enclosure-Base-v1.0 | 1 | 1:10 | 46.15 | 15 | N | 0.20/0.4 | Print with 4 Wall Loops for increased strength
Redwood-Joystick-Enclosure-Top-v1.0 | 1 | 1:58 | 92.84 | 15 | N | 0.20/0.4 | Print with 4 Wall Loops for increased strength
Redwood-Joystick-Topper-Adapter-Cover-v1.0 | 1 | 0:7 | 0.34 | 15 | N | 0.20/0.4 | OPTIONAL
Redwood-Joystick-Topper-Adapter-Nut-v1.0 | 1 | 0:19 | 4.87 | 15 | N | 0.20/0.4 | OPTIONAL

### Post-Processing

Inspect the 3D printed parts for any printing defects, sharp edges, or burrs. Sharp edges and burrs can be removed with sanding or deburring tools. Examples of Quality Prints

## MAKER GUIDE

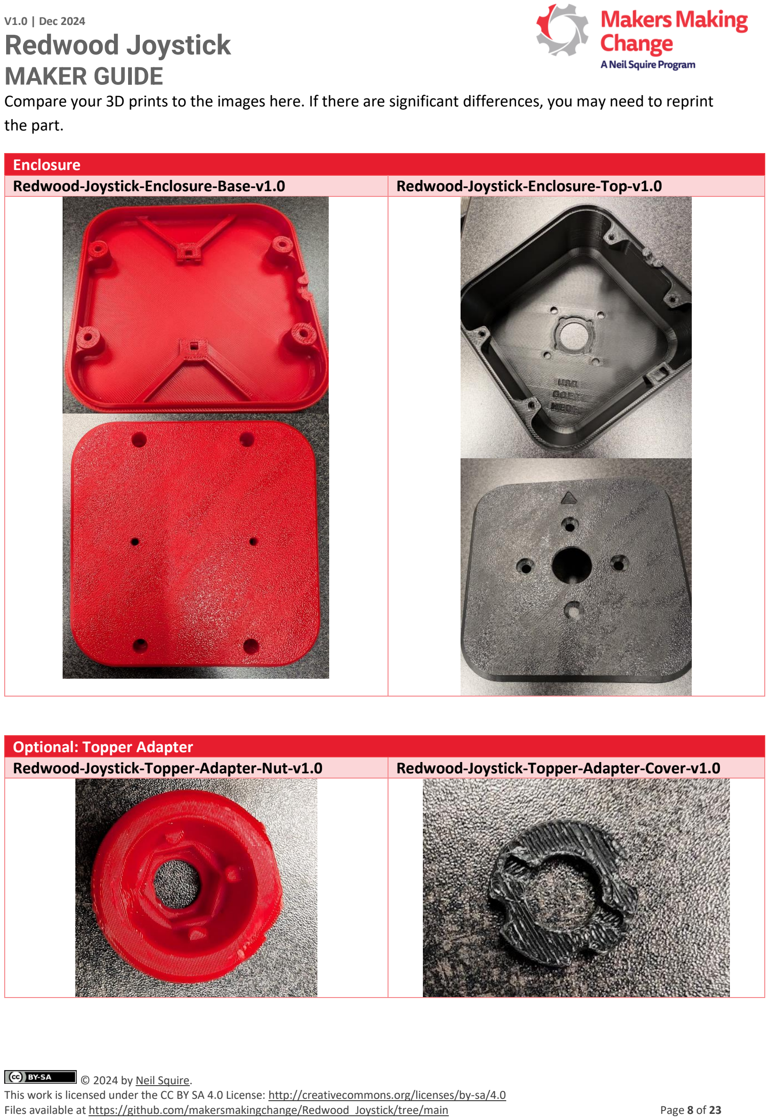
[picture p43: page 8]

Files available at https://github.com/makersmakingchange/Redwood_Joystick/tree/main | Page 8 of 23

Compare your 3D prints to the images here. If there are significant differences, you may need to reprint the part.

Enclosure
Redwood-Joystick-Enclosure-Base-v1.0 | Redwood-Joystick-Enclosure-Top-v1.0

Optional: Topper Adapter
Redwood-Joystick-Topper-Adapter-Nut-v1.0 | Redwood-Joystick-Topper-Adapter-Cover-v1.0

## MAKER GUIDE

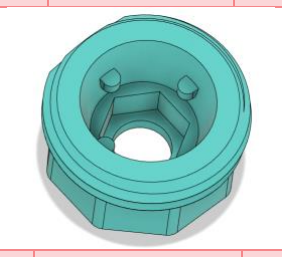
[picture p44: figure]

Files available at https://github.com/makersmakingchange/Redwood_Joystick/tree/main | Page 9 of 23

### Maker Component List

Enclosure
A01 | Screw, #4 self-tapping 3/8" length | QTY: 4 | A02 | UltraStik 360 Joystick Component | QTY: 1 | A03 | Hex nut, M3 | QTY: 2
| | | (joystick component, dust cover, ball top, USB cable)
A04 | Cable tie, 4" | QTY: 1 | A05 | Enclosure Base | QTY: 1 | A06 | Enclosure Top | QTY: 1

*Optional: Topper and Mounting Adapters B01 Metric Hex
Nut M6-
1.00
QTY: 1 | B02 | Topper
Adapter Nut
QTY: 1 | B03 | Topper
Adapter
Cover

QTY: 1

B04 RAM
Mount
Adapter

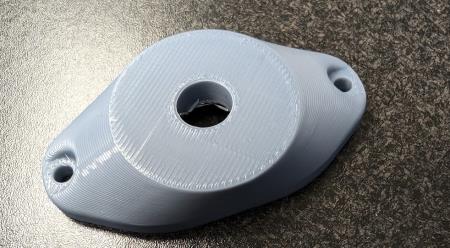
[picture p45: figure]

QTY: 1 | B05 | Camera
Mount
Adapter

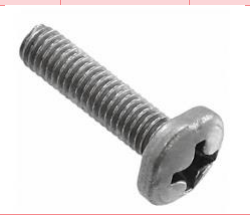
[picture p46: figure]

QTY: 1 | B06 | M3x12mm
Screw

QTY:
2

## MAKER GUIDE

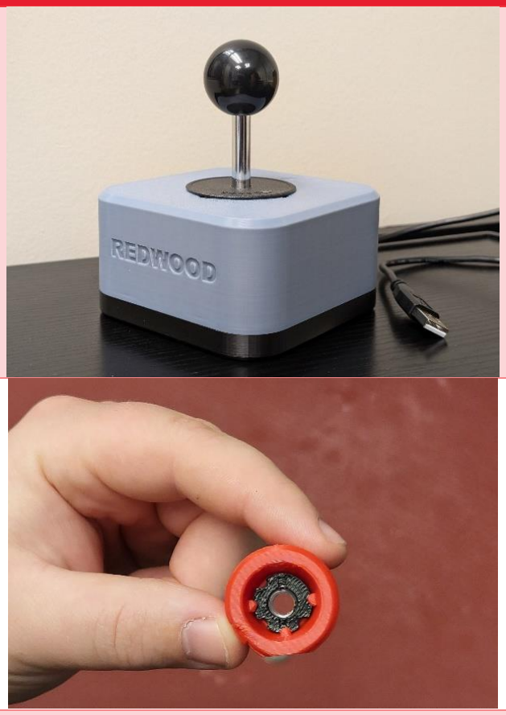
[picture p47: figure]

Files available at https://github.com/makersmakingchange/Redwood_Joystick/tree/main | Page 10 of 23
B07 | 1/4″-20
UNC Tee
Nut Insert,
5/16″
Length
QTY: 1 | B08 | 1/4″-20 Bolt (Any length greater than 10 mm)

QTY: 1

### Assembly Guide

Assembly Section
Part A: Enclosure

OPTIONAL Part B: Topper Adapter

OPTIONAL Part C: Mounting Adapters

## MAKER GUIDE

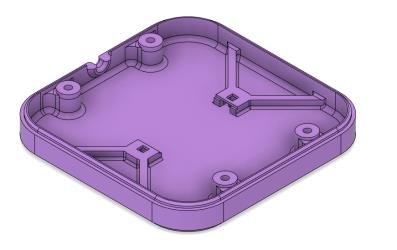
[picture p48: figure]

Files available at https://github.com/makersmakingchange/Redwood_Joystick/tree/main | Page 11 of 23

### Part A: Enclosure

Part A: Required Components
Enclosure
A01 | Screw, #4 self-tapping 3/8" length | QTY: 4 | A02 | UltraStik 360 Joystick Component | QTY: 1 | A03 | Hex nut, M3 | QTY: 2
| | | (joystick component, dust cover, ball top, USB cable)
A04 | Cable tie, 4" | QTY: 1 | A05 | Enclosure Base | QTY: 1 | A06 | Enclosure Top | QTY: 1

Part A: Required Tools and Supplies
- Philips Screw Driver
- 3D printer
- Flush cutters

Part A: Required Personal Protective Equipment (PPE)
- Safety Glasses

## MAKER GUIDE

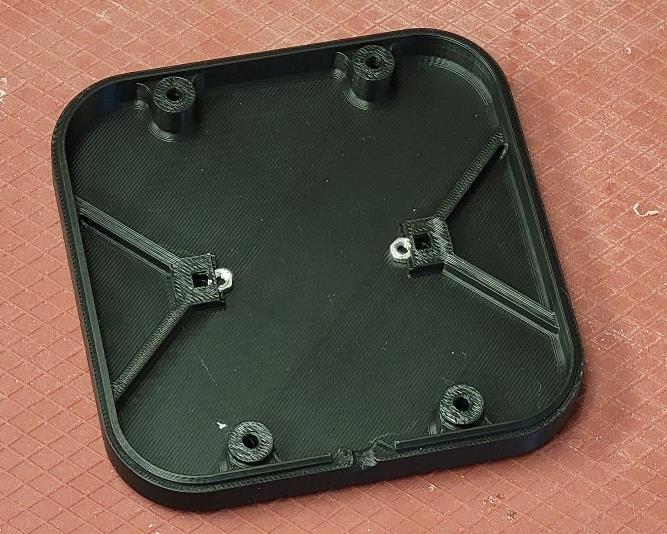
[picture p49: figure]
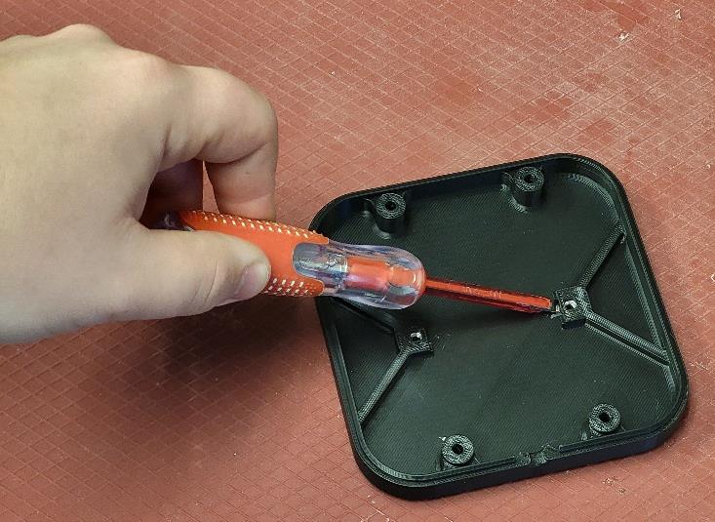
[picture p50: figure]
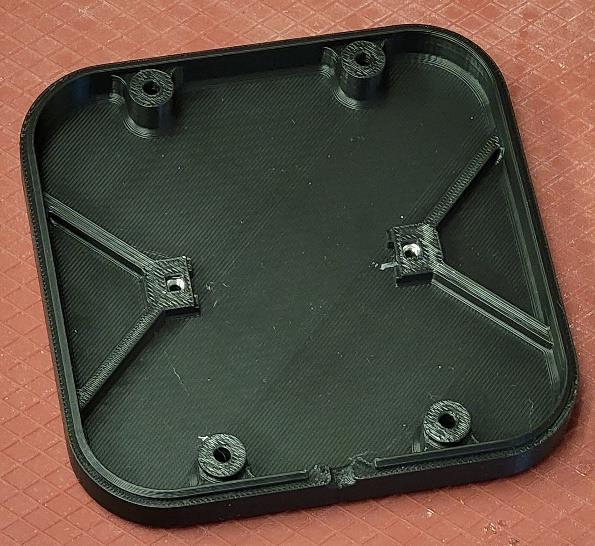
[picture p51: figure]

Files available at https://github.com/makersmakingchange/Redwood_Joystick/tree/main | Page 12 of 23

Part A: Enclosure Assembly Steps

Step A-01: Insert M3 Nuts
Take the enclosure base and locate the two nut catches. Take the 2 M3 hex nuts and insert them into these catches. It is recommended to line them up in the slot and then use the screwdriver to push the hex nuts inside the catches.

## MAKER GUIDE

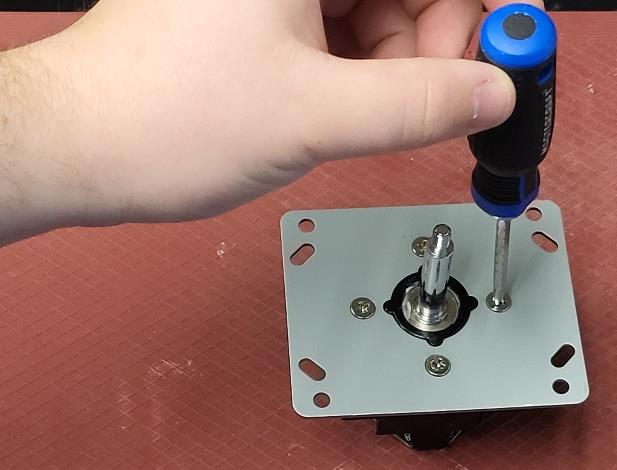
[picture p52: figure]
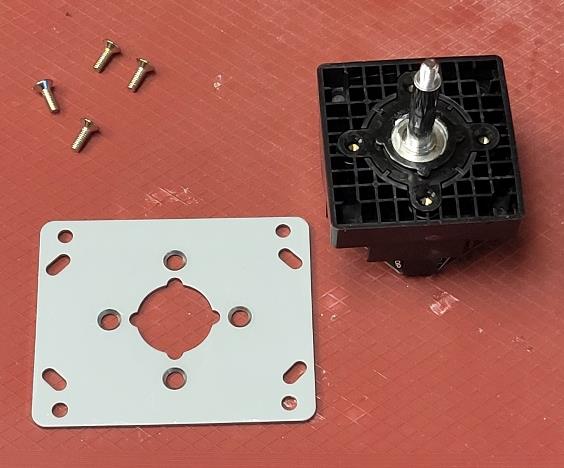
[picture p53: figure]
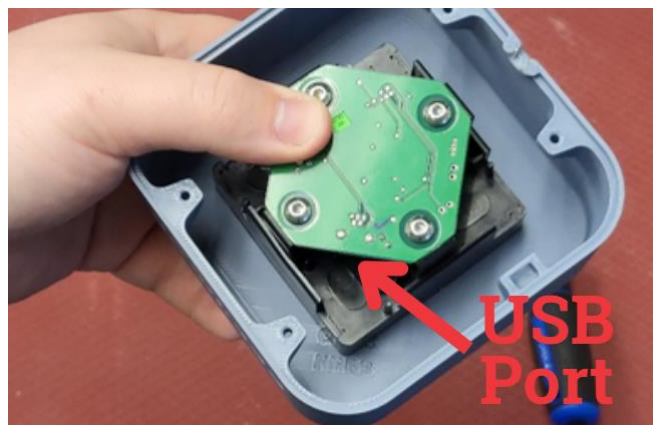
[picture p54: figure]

Files available at https://github.com/makersmakingchange/Redwood_Joystick/tree/main | Page 13 of 23

Step A-02: Remove Mounting Plate from Ultrastik Joystick Component
Take the Ultrastik Joystick component and remove the 4 screws connecting the silver mounting plate to the rest of the joystick. KEEP the 4 screws you removed in a safe place, you will need them for the next step. You can disregard the mounting plate for the rest of the build.

Step A-03: Placing Joystick to Top Enclosure
Take the top enclosure and place the Ultrastik Joystick component inside with the USB port on the joystick component in the corner with the text on the inside of the top enclosure that says “USB GOES HERE”. This must be aligned to ensure proper directionality of the joystick.

## MAKER GUIDE

Files available at https://github.com/makersmakingchange/Redwood_Joystick/tree/main | Page 14 of 23

Step A-04: Attaching Joystick to Top Enclosure
Take the 4 screws that you removed in Step 2 and insert them into the holes on the outer top of the top enclosure. Use the Philips Screwdriver to screw them through the top enclosure and into the Ultrastik Joystick component.

Make sure that the screws are sunken into the top of the housing. Approx 1 mm.

## MAKER GUIDE

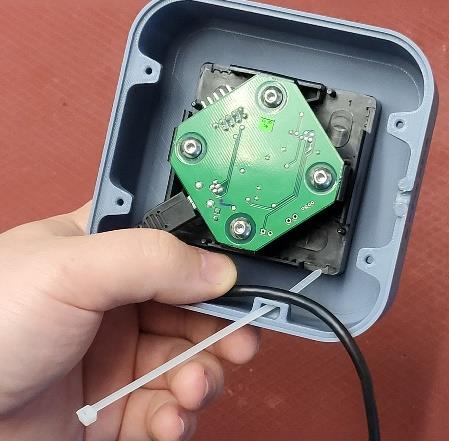
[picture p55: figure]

Files available at https://github.com/makersmakingchange/Redwood_Joystick/tree/main | Page 15 of 23

Step A-05: Attaching the USB Cable
Take the USB cable and attach it to the USB port on the Ultrastik Joystick component. Take the cable tie and pass it through the strain relief feature and attach the USB cable to the side of it. Tighten down the cable tie and use the flush cutters to cut off the excess.

## MAKER GUIDE

Files available at https://github.com/makersmakingchange/Redwood_Joystick/tree/main | Page 16 of 23

Step A-06: Attaching the Bottom Enclosure
Take the bottom enclosure component and fit it to the top component with the cable exit lining up. Take the 4 #4 screws and screw them into the 4 holes on the bottom of the bottom enclosure. Tighten until snug.

## MAKER GUIDE

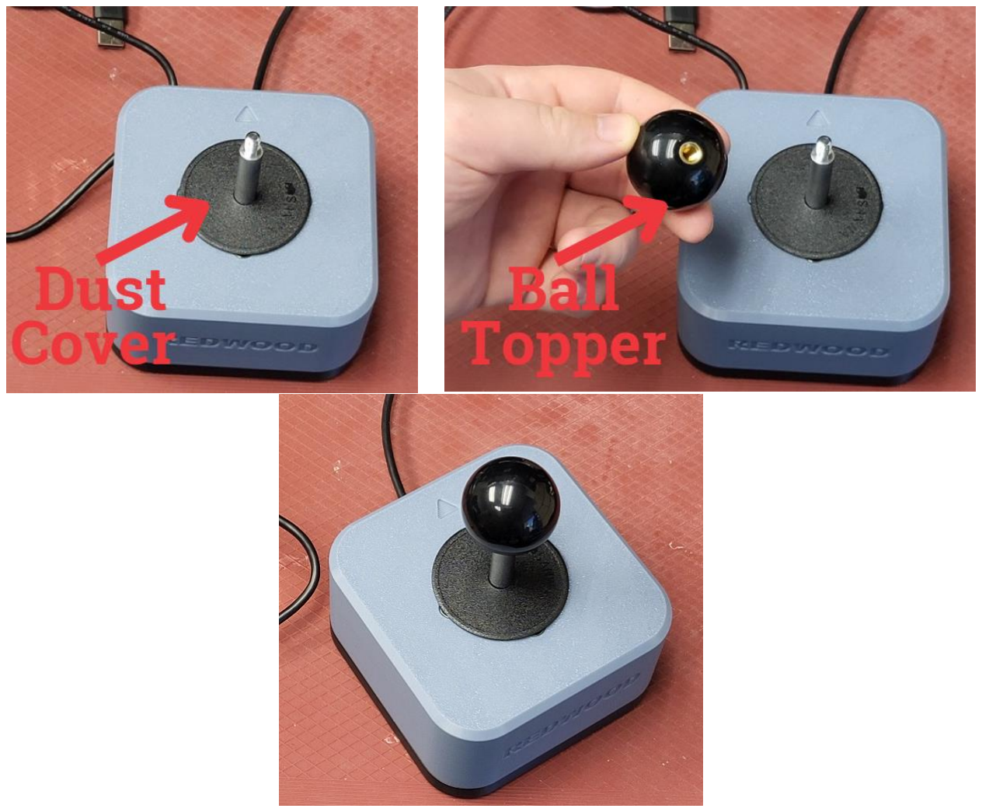
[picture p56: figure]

Files available at https://github.com/makersmakingchange/Redwood_Joystick/tree/main | Page 17 of 23

Step A-07: Add the Dust Cover and Ball Topper
Take the dust cover and ball topper from the Ultrastik and add them to the joystick. Place the dust cover on first and then thread on the ball topper.

## MAKER GUIDE

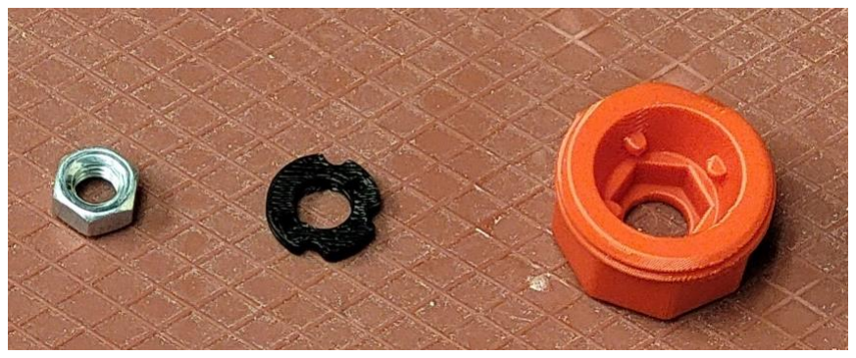
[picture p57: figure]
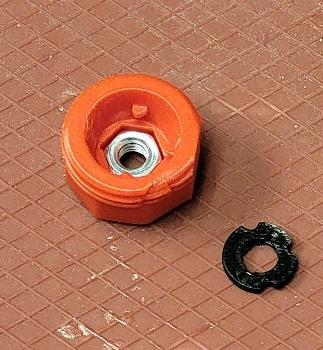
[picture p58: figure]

Files available at https://github.com/makersmakingchange/Redwood_Joystick/tree/main | Page 18 of 23

### Part B: Topper and Mounting Adapters (OPTIONAL)

This section is only needed if the user wants to use Oak Joystick toppers on with the Redwood.

Part B: Required Components
B01 Metric Hex
Nut M6-
1.00
QTY: 1 | B02 | Topper
Adapter
Nut
QTY: 1 | B03 | Topper
Adapter
Cover

QTY: 1

Part B: Required Tools and Supplies
- Philips screw driver
- 3D printer
- Optional: Canadian small coin (dime)

Part B: Required Personal Protective Equipment (PPE)
- None

Part B: Topper Adapter Assembly Steps

Step B -01: Insert M6 Nut
Take the Topper Adapter Nut 3D print and place it on the table with the thread side facing up. Place the M6 nut into the top of the Topper Adapter Nut. Make sure to line it up so the M6 nut sits flush inside.

## MAKER GUIDE

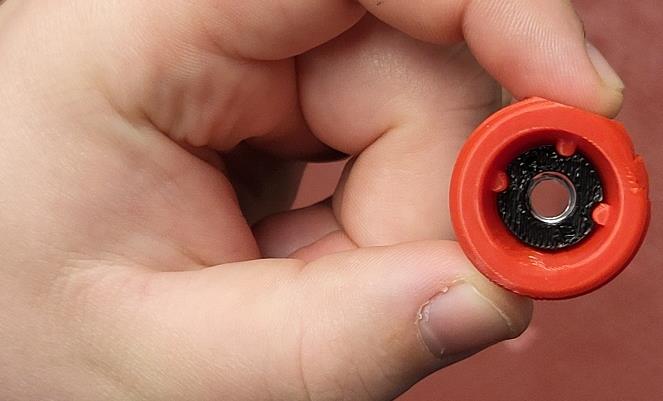
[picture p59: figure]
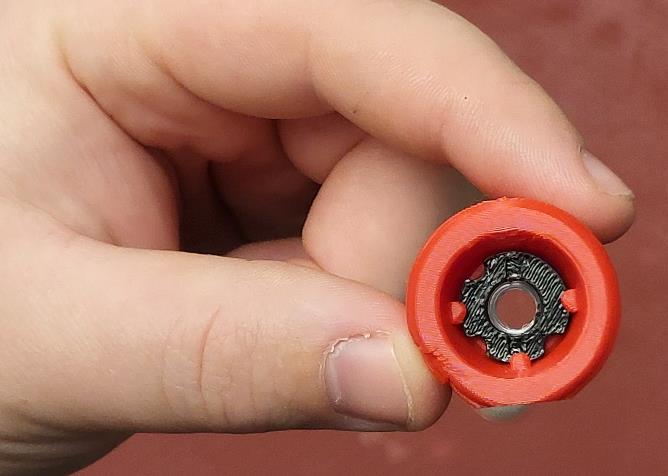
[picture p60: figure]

Files available at https://github.com/makersmakingchange/Redwood_Joystick/tree/main | Page 19 of 23

Step B -02: Add Topper Adapter Cover
Take the Topper Adapter Cover and place it on top of the M6 nut with the slot side facing up. Line up the three stubs on the Topper Adapter Nut with the three cutouts on the Topper Adapter cover.

Step B -03: Secure M6 Nut
Use a small coin, screwdriver, or any tool you can use to rotate the Topper Adapter Cover so then the three stubs and cutouts are not lined up. This will lock in the M6 Nut making it easier to screw onto the Ultrastik joystick.

You can now easily screw this onto the Ultrastik joystick threaded stick.

## MAKER GUIDE

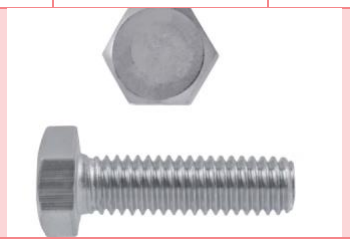
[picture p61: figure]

Files available at https://github.com/makersmakingchange/Redwood_Joystick/tree/main | Page 20 of 23

### Part C: Mounting Adapters (OPTIONAL)

This section is only needed if the user wants to connect the Redwood to a 1/4 -20 camera mount or 1 inch RAM mount.

If the joystick needs to be mounted on a RAM style or ¼-20 camera mount, please assemble one of the adapters. The RAM mount adapter DOES NOT NEED the tee nut insert or ¼-20 bolt.

Part C: Required Components
B04 RAM
Mount
Adapter

QTY: 1 B05 Camera
Mount
Adapter
QTY: 1 | B06 | M3x12mm Screw

QTY:
2

B07 1/4″-20
UNC Tee
Nut Insert,
5/16″
Length
QTY: 1 | B08 | 1/4″-20 Bolt (Any length greater than 10 mm)

QTY: 1

Part C: Required Tools and Supplies
- Plyers to tighten down ¼-20 bolt.
- 3D printer
- Flush cutters to remove any excess filament

Part C: Required Personal Protective Equipment (PPE)
- Safety Glasses

## MAKER GUIDE

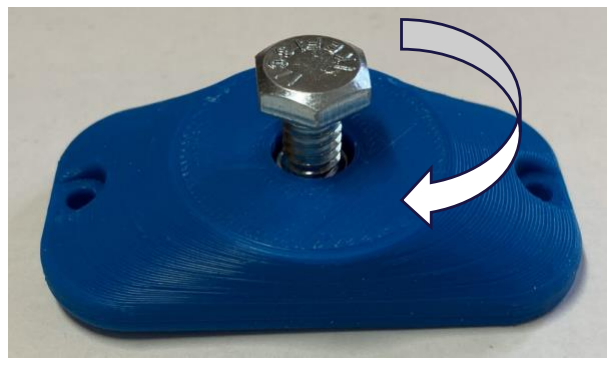
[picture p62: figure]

Files available at https://github.com/makersmakingchange/Redwood_Joystick/tree/main | Page 21 of 23

Part C: Mounting Adapter Steps

Camera Mount Assembly

Step 1: Prepare and Orient 3D Print

Flip the camera mount adapter around to reveal the recess with small slots.

Ensure all supports are removed from the 3D print.

Step 2: Insert Tee Nut

Insert the tee nut, lining up the barbs with the small slots in the 3D print.

Step 3: Screw in Bolt

Flip the part around and screw in a ¼-20 hex bolt.

## MAKER GUIDE

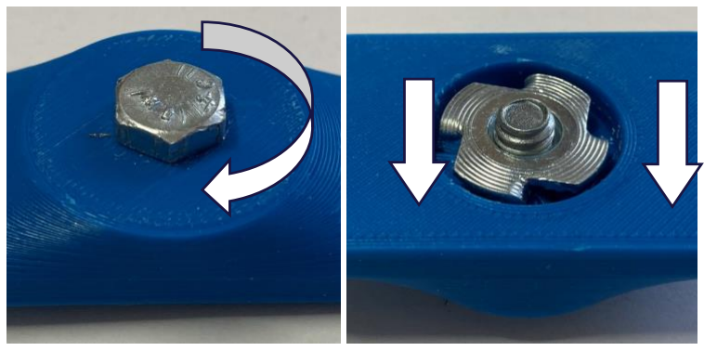
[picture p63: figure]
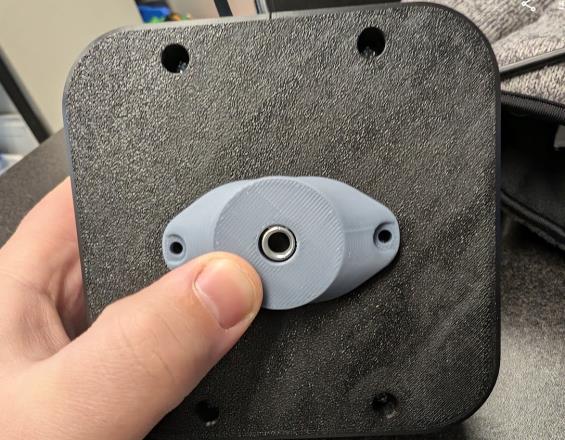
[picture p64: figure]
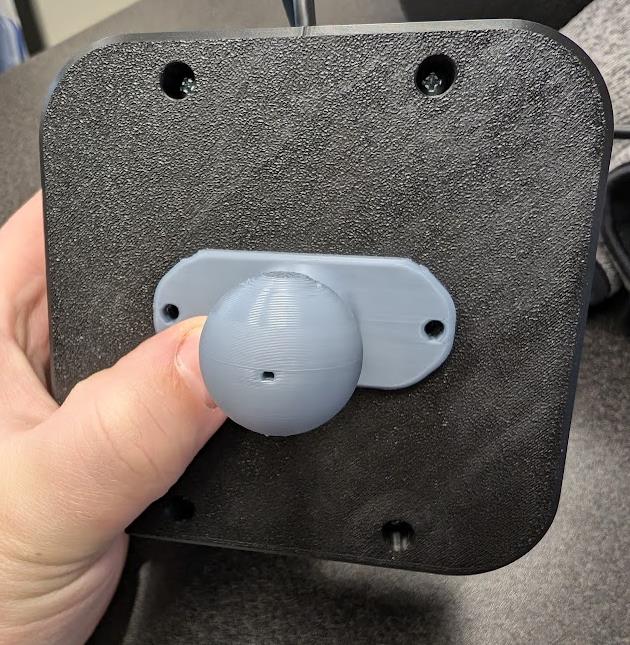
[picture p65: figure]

Files available at https://github.com/makersmakingchange/Redwood_Joystick/tree/main | Page 22 of 23
Step 4: Tighten Bolt

Tighten the bolt until the tee nut is seated down as far as possible.

(Alternatively, if you do not have acces to a bolt, the tee nut may be press fit as long as it sits flush with the 3D print.)

Step 5: Attach to Joystick

Using 2 M3 screws, screw the camera mount adapter to the bottom of the joystick in the two middle holes.

RAM Mount Assembly

Step 1: Attach to Joystick

Using 2 M3 screws, screw the RAM mount adapter to the bottom of the joystick in the two middle holes.

## MAKER GUIDE

Files available at https://github.com/makersmakingchange/Redwood_Joystick/tree/main | Page 23 of 23

### Ultrastik – Oval Version

If you are using the Oval Topper version of the Ultrastik, you will not be able to use the standard topper nut. You will need to go to the alternate part files in the build files to print that file instead. Assembly goes exactly the same except without having a topper adapter cover.

### Testing

You can test using an Xbox Adaptive controller or plugging directly into a PC.

1. Plug the joystick into the analog joystick input for the host device.
a) X1 or X2 on an Xbox Adaptive Controller.
2. Plug the host device into a computer.
3. If using Windows, open “Set up USB Game Controllers” from the Control Panel. You can find this by searching your computer in the search bar next to the Windows icon.
a) If using a Mac, use https://hardwaretester.com/gamepad
4. Select the host device from the list of controllers and go to “Properties”.
5. Move your joystick and observe the movement of the cross hatch in the “Axes” window. Ensure it moves in the proper directions when you move the joystick (the arrow points in the up direction). If not, open the joystick and check your connections.

### Troubleshooting

If your joystick is not moving in the same directions as expected, make sure you have the proper alignment shown in Step A-03: Placing Joystick to Top Enclosure.

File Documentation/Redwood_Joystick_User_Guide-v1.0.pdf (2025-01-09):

V1.0 | Dec 2024

## Redwood Joystick

## USER GUIDE

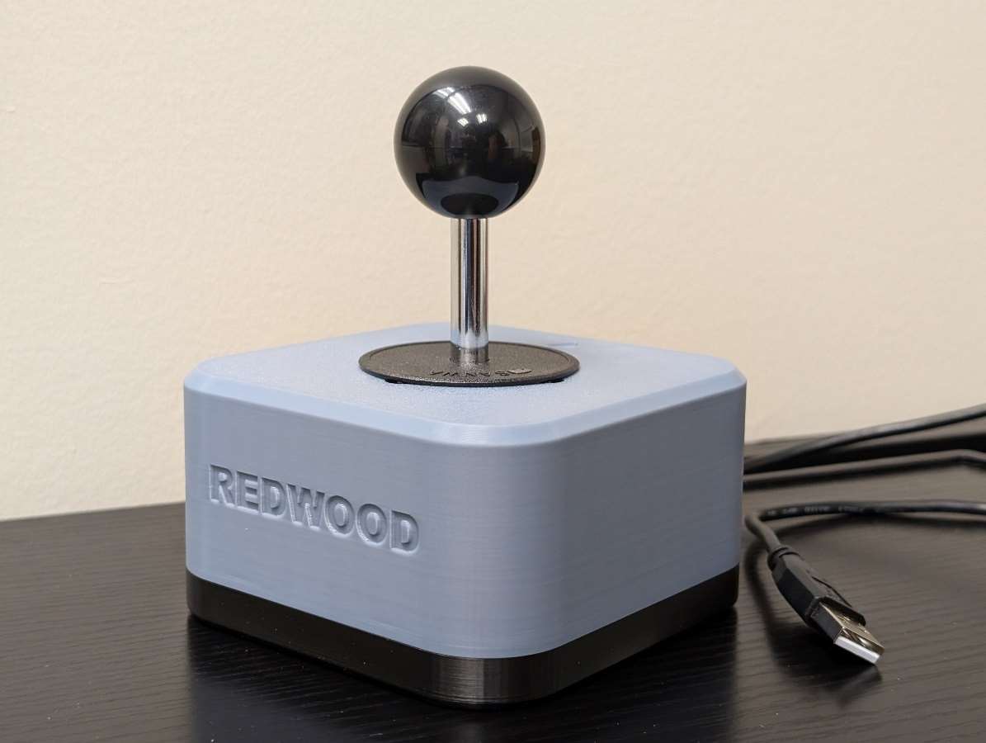
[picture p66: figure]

© 2024 by Neil Squire.
This work is licensed under the CC BY SA 4.0 License: http://creativecommons.org/licenses/by-sa/4.0
Files available at https://github.com/makersmakingchange/Redwood_Joystick/tree/main | Page 1 of 6

### Overview

This document contains the necessary information to use the Redwood Joystick, a robust analog USB joystick that can be used for digital access or adaptive gaming. This design is based off of Ultimarc’s UltraStik 360 joystick (https://www.ultimarc.com/arcade-controls/joysticks/ultrastik-360-oval-top-clone/) and 3D printed enclosure and various toppers have been added to this design.

## USER GUIDE

Files available at https://github.com/makersmakingchange/Redwood_Joystick/tree/main | Page 2 of 6

## Contents

Overview | 1
Introduction | 3
Features | 3
Oak Toppers | 4
Specifications | 4
Compatibility | 5
Usage | 5
UltraMap – Mode Selection | 5
Takedown / Storage | 6
Care | 6
Cleaning | 6
Disposal | 6

## USER GUIDE

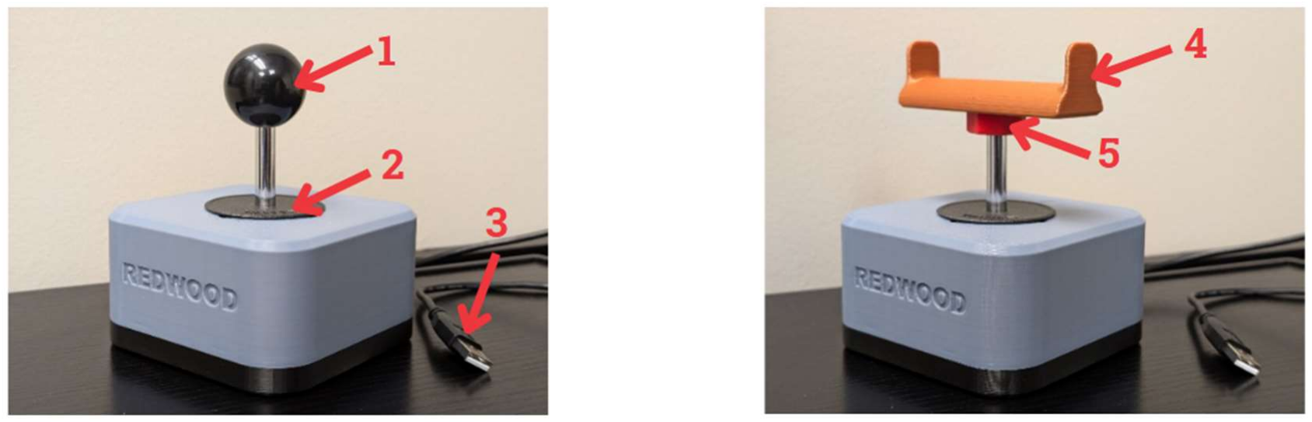
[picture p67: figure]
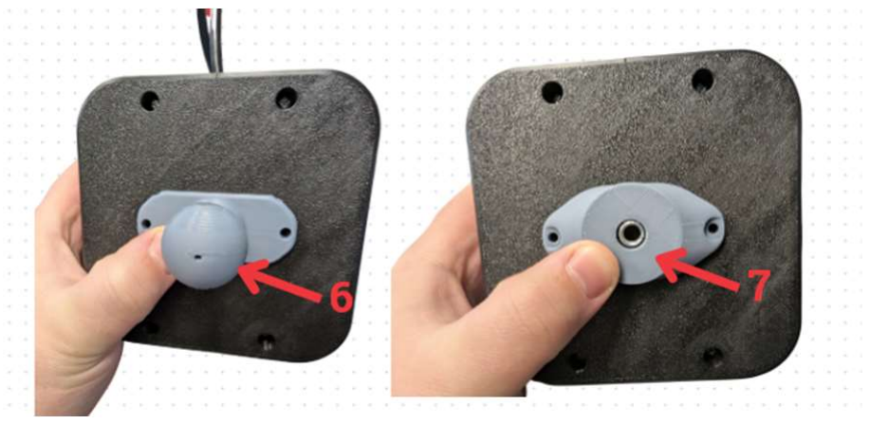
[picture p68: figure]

Files available at https://github.com/makersmakingchange/Redwood_Joystick/tree/main | Page 3 of 6

### Introduction

The Redwood Joystick is a robust analog USB joystick that can be used for digital access or adaptive gaming. The Redwood was designed for users with gross motor movement and high strength that other joysticks may not be able to withstand.

### Features

The Redwood Joystick uses the Ultimarc Ultrastik Joystick as the main internal component. This comes with a default ball topper. If you need other toppers such as goalpost, concave, stick, etc. the Topper Adapter Nut can be used to attach our Oak Joystick toppers. Using the mounting adapters you can mount the joystick on RAM or ¼-20 camera mounts.

Number Feature | Functionality
1 | Ultimarc Ball topper | Default topper that comes with the joystick.
2 | Ultimarc Dust Cover | Prevents dust and grime to enter the inside of the enclosure.
3 | USB Type-A | Allows for connection to devices.
4 | Oak Joystick Toppers | Any of the Oak Joystick toppers will fit the Redwood Joystick using the Topper Adapter Nut. See all small, medium, and large Oak toppers here: https://tinyurl.com/OakTopper
5 | Topper Adapter Nut | Adapter that allows any Oak Joystick topper to fit the Redwood Joystick.
6 | 1 inch RAM Mount Adapter | Can be attached to the bottom of the Redwood Joystick to attach to 1 inch (Type B) RAM mounts.
7 | Camera Mount Adapter | Can be attached to bottom of Redwood Joystick to attach to ¼-20 mounting (common camera mount)

## USER GUIDE

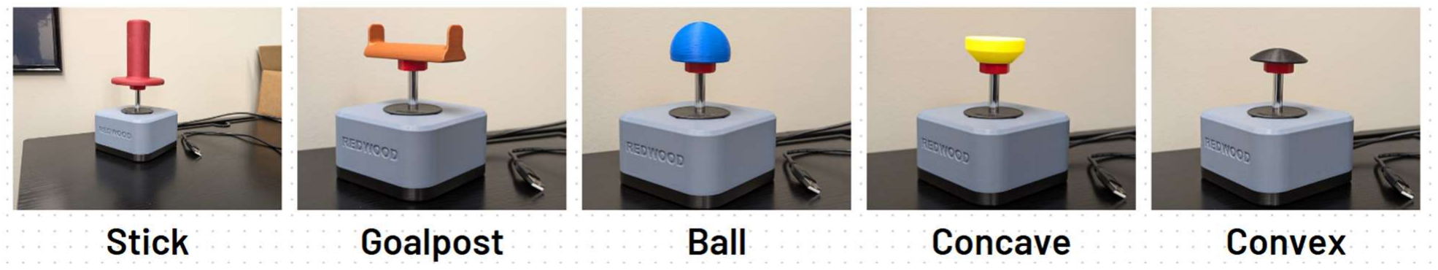
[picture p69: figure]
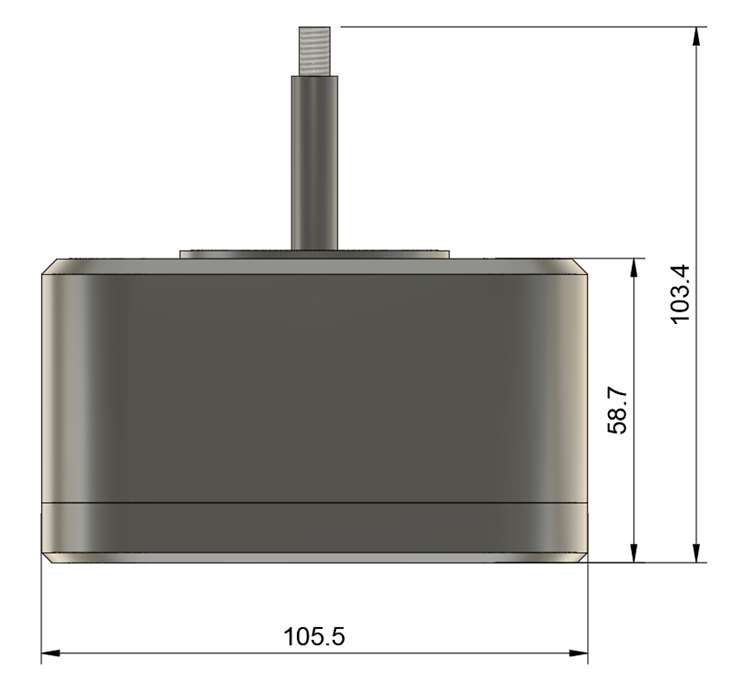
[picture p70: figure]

Files available at https://github.com/makersmakingchange/Redwood_Joystick/tree/main | Page 4 of 6

Oak Toppers
To add any of the Oak toppers, screw on the Topper Adapter Nut to the threads on the stick until secure. Then thread on the Oak topper of your choice.

The Oak Joystick toppers come in a standard small, medium, and large size and can be customized by the maker. There is a stick, goalpost, ball, concave, and convex topper. These are all compatible with the Redwood Joystick using the Topper Adapter Nut. If you are wanting to evaluate the size of the toppers, please see the Oak Joystick Topper Guide: https://github.com/makersmakingchange/Oak-Compact-Joystick/blob/main/Documentation/Oak_Joystick_Topper_Guide.pdf

### Specifications

Item | Redwood Joystick
Size (Length x Width x Height) [mm] | 105.5 x 105.5 x 58.7 (not including height of stick) 105.5 x 105.5 x 103.4 (Including height of stick)
Mass [g] | 274
Type of Cable | USB Type-A
Operating Force (grams) | 298
Range of Motion (degrees) | ±15.5°

## USER GUIDE

Files available at https://github.com/makersmakingchange/Redwood_Joystick/tree/main | Page 5 of 6

### Compatibility

More testing is required to see if the joystick will work on macOS.

Item | Redwood Joystick
PC (Windows XP or Newer) | Yes
macOS | Unknown
IOS | Yes, however only in mouse mode. Using the default analog mode will cause drift. See section below on how to change to mouse mode.
Android (Oreo or newer) | Yes
Xbox Adaptive Controller | Yes
Sony Access Controller | No (Sony Access Controller does not have USB port)
Hori Flex Controller | Yes

### Usage

Connect the Redwood Joystick to your device using the provided USB cable. You may need an adapter or dongle to get the USB connected to your system. The Joystick is by default in Analog Gamepad mode. This means it will act as a joystick for a gamepad system. You can change the mode it is in by using the UltraMap application created by Ultimarc. See the modes available below. Download the software here: https://www.ultimarc.com/arcade-controls/joysticks/ultrastik-360-oval-top-clone/

UltraMap – Mode Selection
By default, the Redwood Joystick will be in Analog mode. The UltraMap application allows you to program the joystick in the following modes:
Mode | Description
2-Way, Up & Down | The joystick restricts movement to only two directions: up and down.
4-Way | Movement is limited to the four cardinal directions: up, down, left, and right.
4-Way, Diagonals Only | Movement is restricted to diagonal directions (e.g., up-right, up-left, down-right, down-left).
8-Way | Full freedom of movement in eight directions: up, down, left, right, and all four diagonals.
8-Way, Easy Diagonals | Similar to 8-Way but optimized for smoother diagonal inputs, reducing the effort required to hit diagonal positions accurately.
Analog | Behaves like a gamepad joystick with proportional controls.
Mouse Pointer | Behaves like a USB mouse pointer. No left or right click buttons included.

To change modes, download the UltraMap application to a computer and plug in the Redwood Joystick. Scan for Ultrastik Joysicks and then select the mapping you want under the “Joystick Map” drop down. Then click the download button and wait for the mode to change. Then, the joystick will behave in that

## USER GUIDE

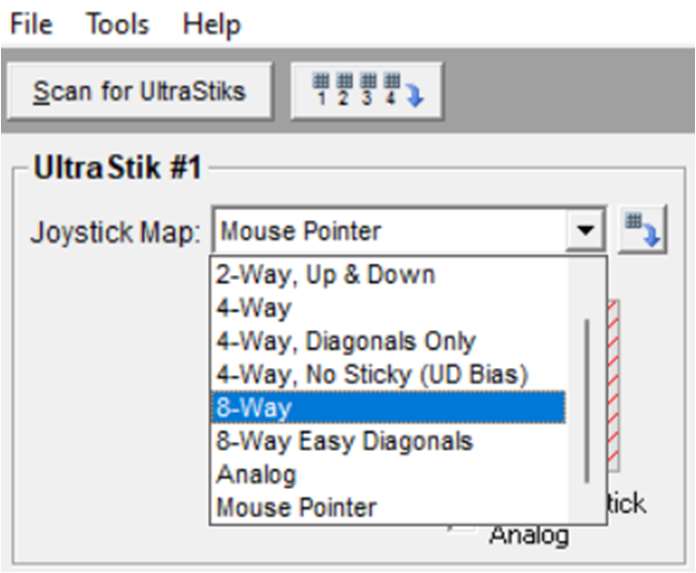
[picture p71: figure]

Files available at https://github.com/makersmakingchange/Redwood_Joystick/tree/main | Page 6 of 6

mode across all devices until you upload a different mode to it. See the Ultrastik installation instructions for more details: https://www.ultimarc.com/arcade-controls/joysticks/ultrastik-360-oval-top-clone/

Takedown / Storage
When not in use, the Redwood Joystick should be stored in a cool place out of direct sunlight.

### Care

The Redwood Joystick is made of 3D printed plastic. Exposure to high heat may cause warping and/or negatively affect function. Extended exposure to sunlight will also weaken the plastic on the device.

The Redwood Joystick contains electronics and is not waterproof. If the device becomes wet, make sure it is off and do not use it until it has completely dried. It may help to open any electronic enclosures to speed up drying and ensure it has completely dried.

Cleaning
The Redwood Joystick can be wiped with a damp cloth. The Redwood Joystick can also be cleaned by scrubbing with warm water and dish soap. Do not use hot water or clean in a dishwasher.

If using warm water and dish soap, ensure any electronic components have been removed before washing.

### Disposal

PLA filament may be industrially compostable in your area. Check with your waste management company if PLA can be composted or must be thrown in the garbage.

Disassemble the Redwood Joystick and separate out the recyclable and compostable components, and those that must be thrown out. Electronics and batteries should be disposed of following your local waste management guidelines.

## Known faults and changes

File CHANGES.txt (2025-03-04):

Version 1.0 | 2025-01-09
 - First publish of the Redwood Joystick
 - Designed enclosure and topper adapter for Ultimarc Ultrastik 360 joystick to have a more robust joystick in the library
 - full documentation was created for this project
 - Both maker and user testing was conducted

Version 1.1 | 2025-03-04
- Created topper nut adapter so the Oval Topper version of the Ultrastik can be used
- Modified documentation to include proper links to the Oval Topper version of the Ultrastik

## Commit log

2024-12-19 Initial Push
    Working files to create github page
    [Button-Regular.iges, Device_Name_BOM.xlsx, OpenAT_Placard.f3d, OpenAT_Placard.stl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]
2025-01-08 Test Push
    Pushing to make sure updates follow
    [Device_Name_BOM.xlsx, Redwood_Joystick_BOM.xlsx]
2025-01-09 Documentation Review Changes
    [Redwood_Joystick_BOM.csv, Redwood_Joystick_BOM.xlsx]
2025-01-09 date change
    date changed to current date
    [Redwood_Joystick_BOM.csv]
2025-03-04 V1.1 Update - Oval Topper Mod Added
    The ball topper version of the joystick was out of stock for a while so we created an alternate version
    that works with the oval topper version.
    The enclosure is the same but the thread for the topper is a M10 not an M6. Therefore, a new topper
    nut was designed. This was just created to have an insert for a M10 nut without the catch.
    Documentation was updated as well.
    [Redwood-Joystick-Topper-Adapter-OvalTopper-v1.0.stl, Redwood_Joystick_BOM-v1.1.csv, Redwood_Joystick_BOM.csv, Redwood_Joystick_BOM.xlsx]
2025-03-11 Oval Topper Adjustment
    Made the entry hole for the thread larger for easier assembly.
    [Redwood-Joystick-Topper-Adapter-OvalTopper-v1.0.stl, Redwood-Joystick-Topper-Adapter-OvalTopper-v1.1.stl]
